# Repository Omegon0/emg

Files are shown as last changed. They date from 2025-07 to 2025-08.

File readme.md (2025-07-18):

# EMGauntlet

Based on project at https://hackaday.io/project/8823-super-simple-muscle-emg-sensor/details

Muscles create many action potentials during a movement, like moving your arm or closing your hands. This creates a measurable signal, which shows an increase in signal due to different fingers moving. (Hackaday)

This project extends the Hackaday project to wirelessly communicate the EMG signals to another device.

Why did I make this? Because it's cool. Also, current medical EMG procedures are more invasive and they hurt so this is a better (albeit less precise) alternative. 

### BOM

|Ref                   |Qnty|Value                      |Cmp name                   |Footprint                                                     |Description                                                                                                           |Vendor |Link                                                                                                                                                |
|----------------------|----|---------------------------|---------------------------|--------------------------------------------------------------|----------------------------------------------------------------------------------------------------------------------|-------|----------------------------------------------------------------------------------------------------------------------------------------------------|
|C1                    |1   |47uF                       |C                          |Capacitor_SMD:C_0805_2012Metric                               |Unpolarized capacitor                                                                                                 |Digikey|https://www.digikey.com/en/products/detail/samsung-electro-mechanics/CL21A476MQYNNNG/3894447                                                        |
|C2, C3, C4, C5, C6, C7|3   |10uF                       |C                          |Capacitor_SMD:C_0805_2012Metric                               |Unpolarized capacitor                                                                                                 |Digikey|https://www.digikey.com/en/products/detail/taiyo-yuden/LMK212BJ106KG-T/930652                                                                       |
|C8, C9                |2   |1uF                        |C                          |Capacitor_SMD:C_0805_2012Metric                               |Unpolarized capacitor                                                                                                 |Digikey|https://www.digikey.com/en/products/detail/samsung-electro-mechanics/CL21B105KBFNNNE/3886687                                                        |
|D1                    |1   |D                          |D                          |Diode_SMD:D_0805_2012Metric                                   |Diode                                                                                                                 |Digikey|https://www.digikey.com/en/products/detail/kyocera-avx/SD0805S020S0R5/3749524                                                                       |
|D2                    |1   |LED                        |LED                        |LED_SMD:LED_0805_2012Metric                                   |Light emitting diode                                                                                                  |Digikey|https://www.digikey.com/en/products/detail/ams-osram-usa-inc/LG-R971-KN-1-0-20-R18/1227925                                                          |
|D3                    |1   |D_Schottky                 |D_Schottky                 |Diode_SMD:D_SMA                                               |Schottky diode                                                                                                        |Digikey|https://www.digikey.com/en/products/detail/mcc-micro-commercial-components/SK54A-LTP/5114132?s=N4IgTCBcDaIMoGkCsAWAggWgDIBUAKIAugL5A                |
|J1                    |1   |Conn_01x02_Pin             |Conn_01x02_Pin             |Connector_JST:JST_PH_S2B-PH-SM4-TB_1x02-1MP_P2.00mm_Horizontal|Generic connector, single row, 01x02, script generated                                                                |Digikey|https://www.digikey.com/en/products/detail/jst-sales-america-inc/S2B-PH-SM4-TB/926655?s=N4IgTCBcDaIMpgEIFoAKAJZcCyAWZAKogBQAyAYgJTFwBylIAugL5A      |
|J3                    |1   |USB_C_Receptacle_USB2.0_16P|USB_C_Receptacle_USB2.0_16P|Connector_USB:AMPHENOL_12402012E212A                          |USB 2.0-only 16P Type-C Receptacle connector                                                                          |Digikey|https://www.digikey.com/en/products/detail/amphenol-cs-commercial-products/12402012E212A/13683192                                                   |
|R1                    |1   |5.7k                       |R                          |Resistor_SMD:R_0805_2012Metric                                |Resistor                                                                                                              |Amazon |https://www.amazon.com/Yobett-ohm-8850pcs-Resistor-Sample/dp/B013B55KQE?source=ps-sl-shoppingads-lpcontext&ref_=fplfs&smid=A3SC7BPT5ZUZY6&gQT=1&th=1|
|R2                    |1   |1k                         |R                          |Resistor_SMD:R_0805_2012Metric                                |Resistor                                                                                                              |Amazon |https://www.amazon.com/Yobett-ohm-8850pcs-Resistor-Sample/dp/B013B55KQE?source=ps-sl-shoppingads-lpcontext&ref_=fplfs&smid=A3SC7BPT5ZUZY6&gQT=1&th=1|
|R3, R4                |2   |100k                       |R                          |Resistor_SMD:R_0805_2012Metric                                |Resistor                                                                                                              |Amazon |https://www.amazon.com/Yobett-ohm-8850pcs-Resistor-Sample/dp/B013B55KQE?source=ps-sl-shoppingads-lpcontext&ref_=fplfs&smid=A3SC7BPT5ZUZY6&gQT=1&th=1|
|R6, R7, R8            |3   |5.1k                       |R                          |Resistor_SMD:R_0805_2012Metric                                |Resistor                                                                                                              |Amazon |https://www.amazon.com/Yobett-ohm-8850pcs-Resistor-Sample/dp/B013B55KQE?source=ps-sl-shoppingads-lpcontext&ref_=fplfs&smid=A3SC7BPT5ZUZY6&gQT=1&th=1|
|SW1                   |1   |SW_SPST                    |SW_SPST                    |Button_Switch_SMD:SW_DPDT_CK_JS202011JCQN                     |Single Pole Single Throw (SPST) switch                                                                                |Digikey|https://www.digikey.com/en/products/detail/c-k/JS202011JCQN/6137630?s=N4IgTCBcDaIFIGUwAYUEY1wMIEUByIAugL5A                                          |
|SW3, SW4              |2   |SW_Push                    |SW_Push                    |Button_Switch_SMD:SW_TS04-66-50-BK-160-SMT                    |Push button switch, generic, two pins                                                                                 |Digikey|https://www.digikey.com/en/products/detail/cts-electrocomponents/222AMVBAR/5227982                                                                  |
|U1                    |1   |INA128                     |INA128UA                   |Package_SO:SOIC-8-1EP_3.9x4.9mm_P1.27mm_EP2.29x3mm            |Precision, Low Power Instrumentation Amplifier G = 1 + 50kOhm/Rg, DIP-8/SOIC-8                                        |Digikey|https://www.digikey.com/en/products/detail/texas-instruments/INA128UA/300997                                                                        |
|U3                    |1   |MCP73831T-2ACI_OT          |MCP73831T-2ACI_OT          |open-Smartwatch:SOT-23-5                                      |IC CONTROLLR LI-ION 4.2V SOT23-5                                                                                      |Digikey|https://www.digikey.com/en/products/detail/microchip-technology/MCP73831T-2ACI-OT/964301                                                            |
|U4                    |1   |DMG3415U-7                 |DMG3415U-7                 |Package_TO_SOT_SMD:SOT95P240X105-3N                           |                                                                                                                      |Digikey|https://www.digikey.com/en/products/detail/diodes-incorporated/dmg3415u-7/2052768                                                                   |
|U5                    |1   |AP2112K-3.3                |AP2112K-3.3                |Package_TO_SOT_SMD:SOT-23-5                                   |600mA low dropout linear regulator, with enable pin, 3.8V-6V input voltage range, 3.3V fixed positive output, SOT-23-5|Digikey|https://www.digikey.com/en/products/detail/diodes-incorporated/AP2112K-3-3TRG1/4470746?s=N4IgTCBcDaIIIAUwEZlgNIFoDMA6bIAugL5A                       |
|U6                    |1   |ESP32-S3-WROOM-1-N16R2     |ESP32-S3-WROOM-1-N16R2     |RF_Module:ESP32-S3-WROOM-1                                    |                                                                                                                      |Digikey|https://www.digikey.com/en/products/detail/espressif-systems/esp32-s3-wroom-1-n16r8/16162642                                                        |

# Schematic and PCB

Use example circuits. Otherwise you might end up learning too much electrical engineering and that's not good! 
Hardest part was figuring out the footprints because most of the components I used were not in Kicad and its just annoying
PCB was wired up using FreeRouting

# Firmware

Just used the analog read program built into Arduino IDE to collect data

# CAD

This depends HEAVILY on the person and its strongly recommended to use photogrammetry to figure it out properly. Also the electrode placement will vary from person to person. 

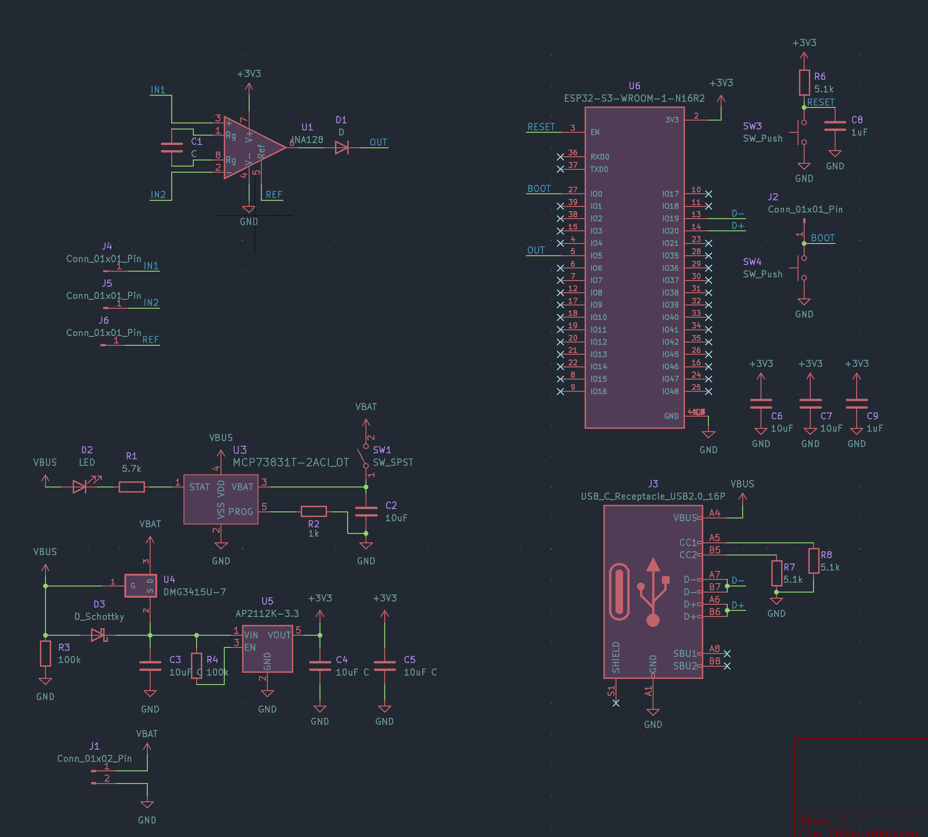
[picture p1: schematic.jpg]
Schematic

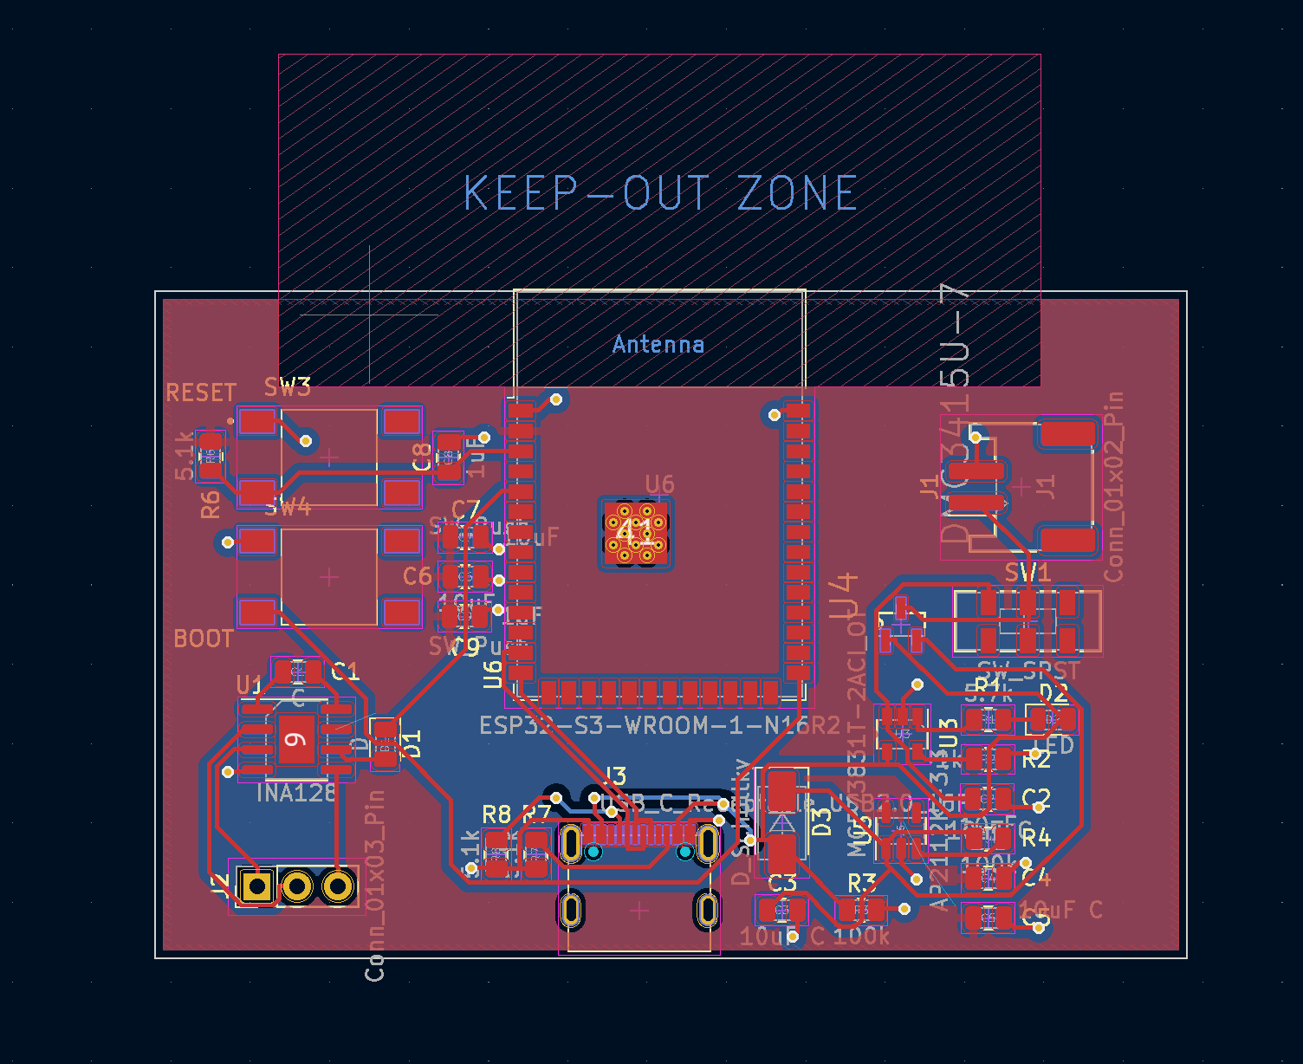
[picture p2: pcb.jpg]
PCB

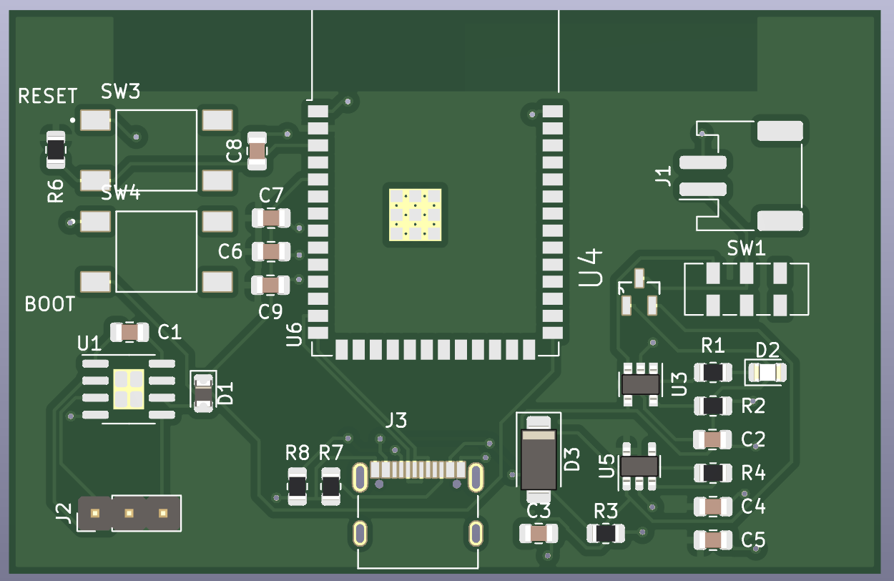
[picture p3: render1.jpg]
render1

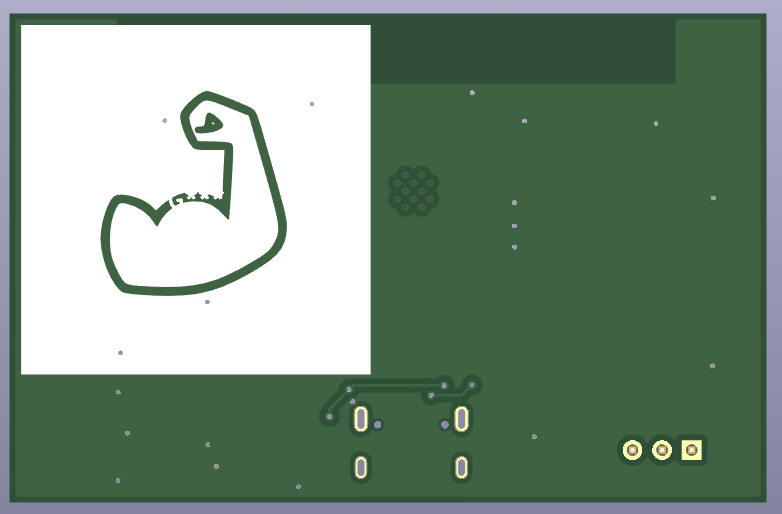
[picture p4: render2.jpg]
render2


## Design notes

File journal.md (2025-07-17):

---
Title: "Muscle EMG sensor"
Author: "Padimo"
Description: "Uses little currents in muscles to detect muscle movement"
Created On: "14/7/2025"
---

# July 12th

Used the Hackaday schematic as a starting point. Also added an ESP32 module and some power management (battery charging and power switching is HARD). Schematic is done, just need to add footprints and then make the PCB.

Schematic

Time spent: 4h

# July 13th

Fixed all errors and passed ERC. Also added footprints to all components. 
Threw stuff into PCB, organized everything, and autorouted. Everything fits onto the top layer 65mmx42mm!
It's looking more like a gauntlet sort of than a slim band but that's ok since it's using a lot of larger components. 

PCB

Time spent: 5h

# July 14th

Caught a few mistakes here and there, and generated production files. Still need to mess around with JLCPCB assembly and see what can be done there.

Time spent: 2h

# July 15th

Made BOM from scratch because I didn't know Kicad could do it. For the IC footprints that I used, I don't know the pitch... I'll need to fix everything with the INA128.

Time spent: 4h

# July 16th

Done with BOM, fixed everything. But there were some crazy high MOQs so I found ones that didn't have that. 

Some components are to be hand soldered: resistors and the power switch. The "additional BOM" is here:

---
| Item | Quantity | Price | Link |
|----------|------------|----------|--------|
| JS202011JCQN | 1 | 0.84 | https://www.digikey.com/en/products/detail/c-k/JS202011JCQN/6137630?s=N4IgTCBcDaIFIGUwAYUEY1wMIEUByIAugL5A |
| 0805 resistors | 1 | depends but I have them | N/A |
| tactile switches | 2 | again, depends but I have them | https://www.digikey.com/en/products/detail/cts-electrocomponents/222AMVBAR/5227982 | 
| ESP32 S3 N16 | 1 | 5.92 | https://www.digikey.com/en/products/detail/espressif-systems/ESP32-S3-WROOM-1-N16/16162647 |
| SD0805S020S0R5 | 1 | 0.34 | https://www.digikey.com/en/products/detail/kyocera-avx/SD0805S020S0R5/3749524 | 
---

Also J2 is supposed to be a solderable header so nothing is needed there

### Problems
I uploaded everything to JLCPCB and it turns out that the ESP can't be mounted with economic assembly so that's another one to add to the list. 
Diode that I used was a BAT54 but the footprint was 0805 and its better to do that on my own so that's added to this extra BOM
Some ICs were rotated -90 degrees so I fixed that in the CLS file

I am now discovering the extended component fee. I'm switching to stencil and doing it myself, and I'll figure it all out tomorrow

Time spent: 6h

# July 17

Switching the project to Highway so I can get more funding. 
I can now get everything assembled in PCBA ideally (except the resistors because JLC genuinely doesn't have most of them)
BOM updated to have every part
Got renders of the PCB
Also there's no case/CAD because electrode placement varies from person to person. 

render1
render2

Time spent: 4h

**Total time spent: 25h**

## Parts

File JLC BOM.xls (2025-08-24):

Comment | Designator | Footprint | JLCPCB Part#(optional)
INA128 | U1 | SOIC-8 | C1346225
MCP73831T-2ACI_OT | U3 | SOT-23-5 | C424093
DMG3415U-7 | U4 | SOT-23 | C96616
AP2112K-3.3 | U5 | SOT-23-5 | C23380830
ESP32-S3-WROOM-1-N16R2 | U6 | SMD | C2913199
47uF | C1 | 0805 | C76636
10uF | C2 | 0805 | C40894
10uF | C3 | 0805 | C40894
10uF | C4 | 0805 | C40894
10uF | C5 | 0805 | C40894
10uF | C6 | 0805 | C40894
10uF | C7 | 0805 | C40894
1uF | C8 | 0805 | C5422
1uF | C9 | 0805 | C5422
KT-0805G | D2 | 0805 | C2297
SK54A-LTP | D3 | SMA(DO-214AC) | C669017
S2B-PH-SM4-TB(LF)(SN) | J1 | SMD | C295747
Amphenol ICC | J3 | SMD | C5150972
SPST | SW1 | SMD | C221665

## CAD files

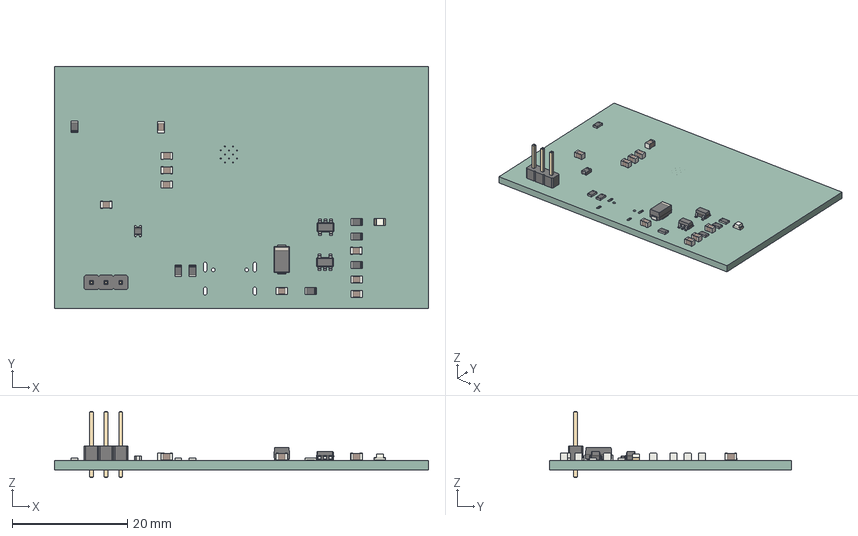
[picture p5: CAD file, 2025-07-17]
EMGauntlet.step
65.0 x 42.0 x 11.5 mm
R_0805_2012Metric x 7
PinHeader_1x03_P254mm_Vertical
D_SMA
C_0805_2012Metric x 9
SOT_23_5 x 2
D_0805
LED_0805_2012Metric
EMGauntlet PCB

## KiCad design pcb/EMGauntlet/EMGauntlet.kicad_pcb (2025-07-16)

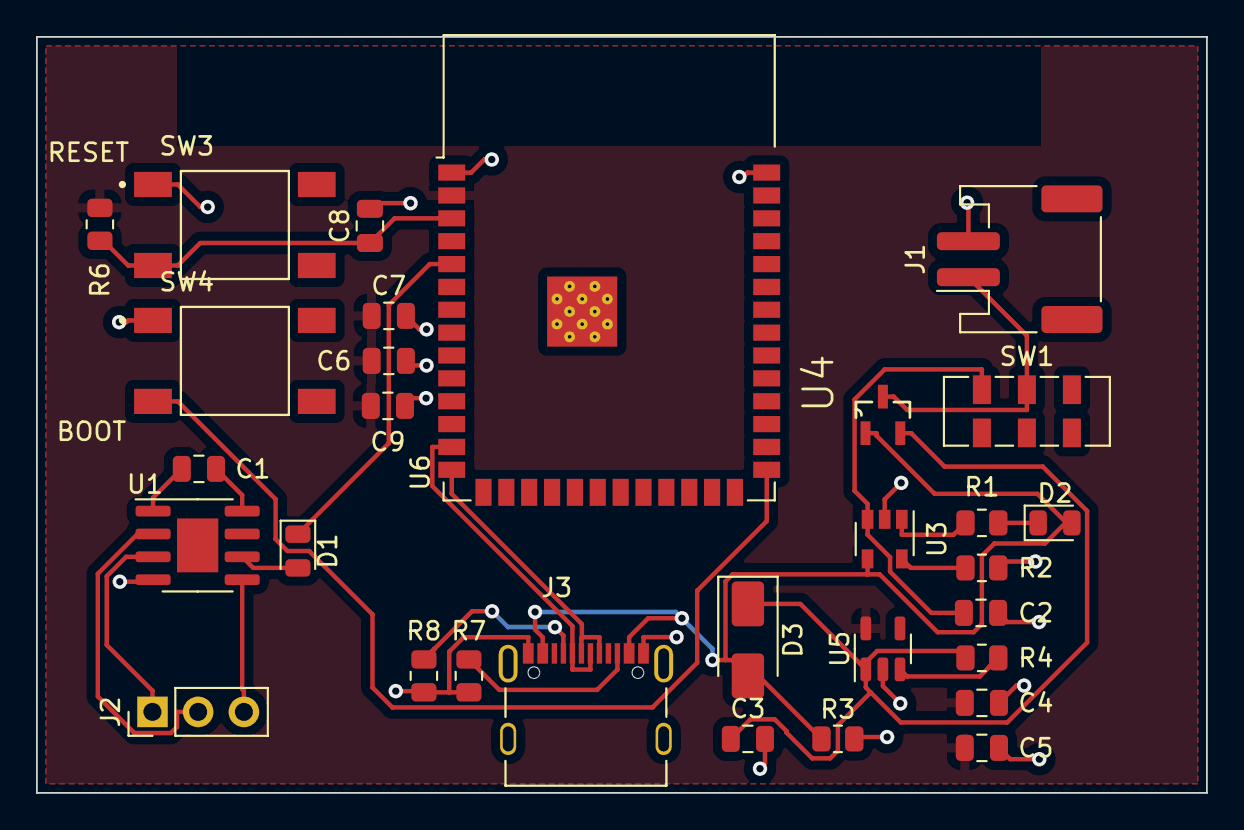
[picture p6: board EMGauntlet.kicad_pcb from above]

Board: 2 copper layers, 65.0 x 42.0 mm, 30 parts (0 on the bottom side), 23 nets.

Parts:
C1: C; C_0805_2012Metric
C2, C6, C7: 10uF; C_0805_2012Metric
C3, C4, C5: 10uF C; C_0805_2012Metric
C8, C9: 1uF; C_0805_2012Metric
D1: D; D_0805_2012Metric
D2: LED; LED_0805_2012Metric
D3: D_Schottky; D_SMA
J1: Conn_01x02_Pin; JST_PH_S2B-PH-SM4-TB_1x02-1MP_P2.00mm_Horizontal
J2: Conn_01x03_Pin; PinHeader_1x03_P2.54mm_Vertical
J3: USB_C_Receptacle_USB2.0_16P; AMPHENOL_12402012E212A
R1: 5.7k; R_0805_2012Metric
R2: 1k; R_0805_2012Metric
R3, R4: 100k; R_0805_2012Metric
R6, R7, R8: 5.1k; R_0805_2012Metric
SW1: SW_SPST; SW_DPDT_CK_JS202011JCQN
SW3, SW4: SW_Push; SW_TS04-66-50-BK-160-SMT
U1: INA128; SOIC-8-1EP_3.9x4.9mm_P1.27mm_EP2.29x3mm
U3: MCP73831T-2ACI_OT; SOT-23-5
U4: DMG3415U-7; SOT95P240X105-3N
U5: AP2112K-3.3; SOT-23-5
U6: ESP32-S3-WROOM-1-N16R2; ESP32-S3-WROOM-1

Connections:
+3V3: C4.1, C5.1, C6.1, C7.1, C9.1, R6.1, U1.7 (V+), U5.5 (VOUT), U6.2 (3V3)
/BOOT: SW4.2, U6.27 (IO0)
/D+: J3.A6 (D+), J3.B6 (D+), U6.14 (IO20)
/D-: J3.A7 (D-), J3.B7 (D-), U6.13 (IO19)
/IN1: J2.1, U1.3 (+)
/IN2: J2.2, U1.2 (-)
/OUT: D1.1 (K), U6.5 (IO5)
/REF: J2.3, U1.5 (Ref)
/RESET: C8.1, R6.2, SW3.2, U6.3 (EN)
GND: C2.2, C3.2, C4.2, C5.2, C6.2, C7.2, C8.2, C9.2, J1.2, J3.A1 (GND), J3.B1 (GND), R2.2, R3.2, R7.2, R8.2, SW3.1, SW4.1, U1.4 (V-), U3.2 (VSS), U5.2 (GND), U6.1 (GND), U6.40 (GND)
unnamed: C1.1, U1.1 (Rg)
unnamed: C1.2, U1.8 (Rg)
unnamed: D1.2 (A), U1.6
unnamed: D2.1 (K), R1.1
unnamed: C3.1, D3.1 (K), R4.1, U4.2 (S), U5.1 (VIN)
unnamed: J3.A5 (CC1), R8.1
unnamed: J3.B5 (CC2), R7.1
unnamed: C2.1, SW1.1 (A), U3.3 (VBAT)
unnamed: R2.1, U3.5 (PROG)
unnamed: R1.2, U3.1 (STAT)
unnamed: R4.2, U5.3 (EN)
VBAT: J1.1, SW1.2 (B), U4.3 (D)
VBUS: D2.2 (A), D3.2 (A), J3.A4 (VBUS), J3.B4 (VBUS), R3.1, U3.4 (VDD), U4.1 (G)

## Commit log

2025-07-16 added pcb files
    [BOM.xls, EMGauntlet-B_Cu.gbr, EMGauntlet-B_Mask.gbr, EMGauntlet-B_Paste.gbr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]
2025-07-16 added bom and journal updates
    [BOM.xls]
2025-07-16 updated bom and journal
    [BOM.xls]
2025-07-16 updated journal
    [BOM.xls, EMGauntlet-all-pos.csv]
2025-07-17 updated journal and readme, added renders, full BOM
    [BOM.xls, EMGauntlet.csv, EMGauntlet.step, JLC BOM.xls]
2025-07-19 fixed bom
    [bom.csv]
2025-07-23 pcba bom
    [bom.csv]
2025-08-24 file dump
    [JLC BOM.xls]
